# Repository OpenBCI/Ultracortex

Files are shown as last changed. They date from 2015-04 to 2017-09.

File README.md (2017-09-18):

# Ultracortex

Ultracortex Mark Numbers (aka versions)

* [Mark 1](https://github.com/OpenBCI/Ultracortex/tree/master/Mark_1) - designed, printed, assembled, & modeled (April 2015)
* [Mark 2](https://github.com/OpenBCI/Ultracortex/tree/master/Mark_2) - designed, printed, assembled, & tested (May-June 2015)
* [Mark 3](https://github.com/OpenBCI/Ultracortex/tree/master/Mark_3) - designed, printed, assembled, & tested (July-September 2015)
* [Mark III "Nova" & "Supernova"](https://github.com/OpenBCI/Ultracortex/tree/master/Mark_III_Nova) - designed, printed, assembled, & tested (April 2016)
* [Mark III "Nova" & "Supernova" (REVISED)](https://github.com/OpenBCI/Ultracortex/tree/master/Mark_III_Nova_REVISED) - designed, printed, assembled, & tested (June 2016)
* [**CURRENT**] [Mark IV](https://github.com/OpenBCI/Ultracortex/tree/master/Mark_IV) - designed, printed, assembled, & tested (January 2017)

The Ultracortex is an open-source, 3D-printable headset intended to work with the [OpenBCI system](http://openbci.com/). It is capable of recording research-grade brain activity (EEG), muscle activity (EMG), and heart activity (ECG). The Ultracortex is under constant iteration. If you print/assemble your own Ultracortex, we would love to hear your feedback. Send us an email at [contact@openbci.com](mailto:contact@openbci.com) or Tweet at us ([@Ultracortex](https://twitter.com/Ultracortex) & [@OpenBCI](https://twitter.com/OpenBCI))!

Designers & Engineers:

* [Aaron Trocola (aka Threeform)](http://threeformfashion.com/)
* [Conor Russomanno](https://twitter.com/russomanno15)
* [Joel Murphy (aka SafeForRobots)](https://twitter.com/safeforrobots)
* [Aaron Lehr](http://aaronlehr.com/portfolio/)

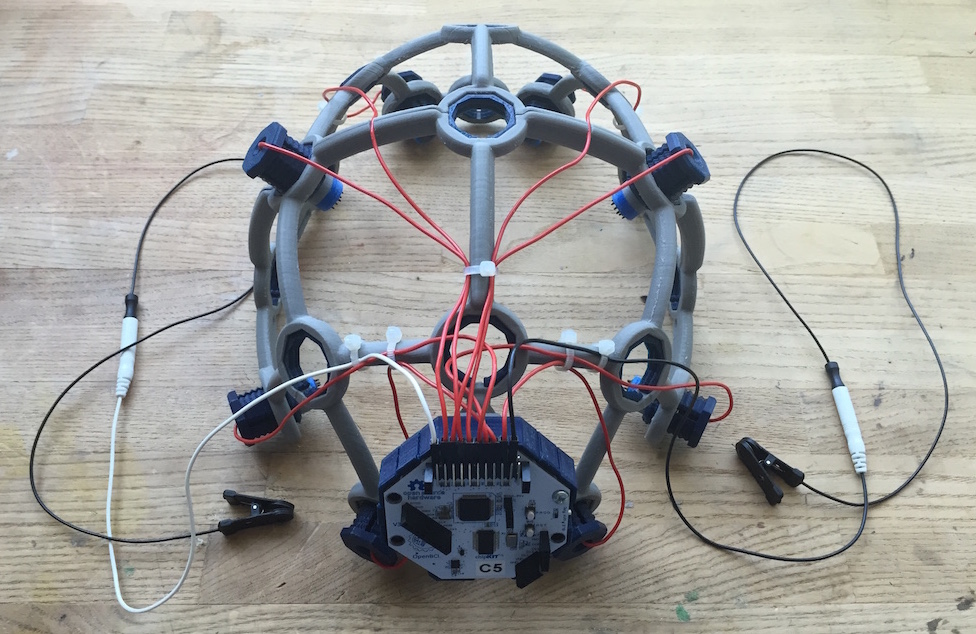
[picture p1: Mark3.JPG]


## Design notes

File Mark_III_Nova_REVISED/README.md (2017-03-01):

#Ultracortex Mark III "Nova" & "Supernova" (REVISED)

*Development Period: June 2016*

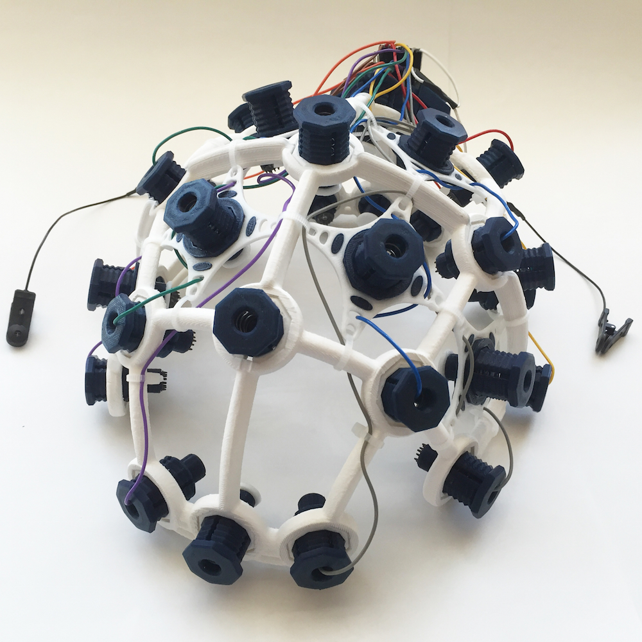
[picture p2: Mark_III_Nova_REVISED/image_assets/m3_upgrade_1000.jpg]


####Complete Ultracortex Mark 3 kits are [available for sale](http://openbci.myshopify.com/collections/frontpage/products/ultracortex-mark-3-eeg-headset-kit-assembly-required) in the OpenBCI Online Store!

The Ultracortex is an open-source, 3D-printable headset intended to work with the [OpenBCI system](http://openbci.com/). It is capable of recording research-grade brain activity (EEG), muscle activity (EMG), and heart activity (ECG). The Ultracortex is under constant iteration. If you print/assemble your own Ultracortex, we would love to hear your feedback. Send us an email at [contact@openbci.com](mailto:contact@openbci.com) or Tweet at us ([@Ultracortex](https://twitter.com/Ultracortex) & [@OpenBCI](https://twitter.com/OpenBCI))!

Designers & Engineers:

* [Aaron Trocola (aka Threeform)](http://threeformfashion.com/)
* [Conor Russomanno](https://twitter.com/russomanno15)
* [Joel Murphy (aka SafeForRobots)](https://twitter.com/safeforrobots)

## THE COMPLETE ULTRACORTEX

**Note:** the part quantities listed below assume you are making an electrode holder for all 21 nodes of the Ultracortex Mark 3. In reality, you will likely have only 8 or 16 electrodes, depending on whether you are working with the [OpenBCI 32bit Board](http://openbci.myshopify.com/collections/frontpage/products/openbci-32-bit-board-kit) (8 channels) or the [OpenBCI 16-channel R&D Kit](http://openbci.myshopify.com/collections/frontpage/products/openbci-16-channel-r-d-kit) (16 channels). You may only want to create as many electrode units as you have channels, and then add more as necessary. In general, more electrodes will distribute the downward scalp pressure, increasing comfort.

###3D-printed Parts:

* [FRAME](https://github.com/OpenBCI/Ultracortex/tree/master/Mark_III_Nova_REVISED/STLs/FRAME) (head circumference: small = 50-55cm, medium = 55-60cm, large = 60-65cm)
	* FRAME_FRONT (**x1**) — .STLs ([small](https://github.com/OpenBCI/Ultracortex/raw/master/Mark_III_Nova_REVISED/STLs/FRAME/small/SMALL_FRONT-M3_Nova_Revised.stl) / [medium](https://github.com/OpenBCI/Ultracortex/raw/master/Mark_III_Nova_REVISED/STLs/FRAME/medium/MEDIUM_FRONT-M3_Nova_Revised.stl) / [large](https://github.com/OpenBCI/Ultracortex/raw/master/Mark_III_Nova_REVISED/STLs/FRAME/large/LARGE_FRONT-M3_Nova_Revised.stl))
	* FRAME_BACK (**x1**) — .STLs ([small](https://github.com/OpenBCI/Ultracortex/raw/master/Mark_III_Nova_REVISED/STLs/FRAME/small/SMALL_BACK-M3_Nova_Revised.stl) / [medium](https://github.com/OpenBCI/Ultracortex/raw/master/Mark_III_Nova_REVISED/STLs/FRAME/medium/MEDIUM_BACK-M3_Nova_Revised.stl) / [large](https://github.com/OpenBCI/Ultracortex/raw/master/Mark_III_Nova_REVISED/STLs/FRAME/large/LARGE_BACK-M3_Nova_Revised.stl))
* [MECH_PARTS](https://github.com/OpenBCI/Ultracortex/tree/master/Mark_III_Nova_REVISED/STLs/MECH_PARTS)
	* [OCTANUT](https://github.com/OpenBCI/Ultracortex/tree/master/Mark_III_Nova_REVISED/STLs/MECH_PARTS/OCTANUT) (**x21**) — .STLs ([tight](https://github.com/OpenBCI/Ultracortex/raw/master/Mark_III_Nova_REVISED/STLs/MECH_PARTS/OCTANUT/OCTANUT-TIGHT.stl) / [normal](https://github.com/OpenBCI/Ultracortex/raw/master/Mark_III_Nova_REVISED/STLs/MECH_PARTS/OCTANUT/OCTANUT-NORMAL.stl) / [loose](https://github.com/OpenBCI/Ultracortex/raw/master/Mark_III_Nova_REVISED/STLs/MECH_PARTS/OCTANUT/OCTANUT-LOOSE.stl)) (Choose normal first / if it is too tight for the OCTABOLT, choose loose / if it is too loose for the OCTABOLT, choose tight)
	* [OCTABOLT](https://github.com/OpenBCI/Ultracortex/blob/master/Mark_III_Nova_REVISED/STLs/MECH_PARTS/OCTABOLT_20.stl) (**x21**) — [.STL download link](https://github.com/OpenBCI/Ultracortex/raw/master/Mark_III_Nova_REVISED/STLs/MECH_PARTS/OCTABOLT_20.stl)
	* [OCTARING](https://github.com/OpenBCI/Ultracortex/blob/master/Mark_III_Nova_REVISED/STLs/MECH_PARTS/OCTARING.stl) (**x21**) — [.STL download link](https://github.com/OpenBCI/Ultracortex/raw/master/Mark_III_Nova_REVISED/STLs/MECH_PARTS/OCTARING.stl)
	* [ELECTRODE_HOLDER](https://github.com/OpenBCI/Ultracortex/blob/master/Mark_III_Nova_REVISED/STLs/MECH_PARTS/E_HOLDER.stl) (**x21**) — [.STL download link](https://github.com/OpenBCI/Ultracortex/raw/master/Mark_III_Nova/STLs/MECH_PARTS/E_HOLDER.stl)
	* [QUADSTAR](https://github.com/OpenBCI/Ultracortex/blob/master/Mark_III_Nova_REVISED/STLs/MECH_PARTS/QUADSTAR.stl) (**x21**) — [.STL download link](https://github.com/OpenBCI/Ultracortex/raw/master/Mark_III_Nova/STLs/MECH_PARTS/QUADSTAR.stl)
	* [Comfy Insert](https://github.com/OpenBCI/Ultracortex/blob/master/Mark_III_Nova_REVISED/STLs/MECH_PARTS/Comfy_Insert.stl) (**x21**) — [.STL download link](https://github.com/OpenBCI/Ultracortex/raw/master/Mark_III_Nova/STLs/MECH_PARTS/Comfy_Insert.stl)	
* [BOARD_HOLDER](https://github.com/OpenBCI/Ultracortex/blob/master/Mark_III_Nova_REVISED/STLs/HOLDER_AND_COVER/BOARD_HOLDER.stl) (**x1**) — [.STL download link](https://github.com/OpenBCI/Ultracortex/raw/master/Mark_III_Nova/STLs/HOLDER_AND_COVER/BOARD_HOLDER.stl)
* BOARD_COVER (**x1**) — choose STANDARD or ADVANCED
	* [STANDARD](https://github.com/OpenBCI/Ultracortex/blob/master/Mark_III_Nova_REVISED/STLs/HOLDER_AND_COVER/BOARD_COVER_STANDARD.stl) — [.STL download link](https://github.com/OpenBCI/Ultracortex/raw/master/Mark_III_Nova/STLs/HOLDER_AND_COVER/BOARD_COVER_STANDARD.stl)
	* [ADVANCED](https://github.com/OpenBCI/Ultracortex/blob/master/Mark_III_Nova_REVISED/STLs/HOLDER_AND_COVER/BOARD_COVER_ADVANCED.stl) (for extra hardware accessibility / if you've soldered on your header rows) — [.STL download link](https://github.com/OpenBCI/Ultracortex/raw/master/Mark_III_Nova/STLs/HOLDER_AND_COVER/BOARD_COVER_ADVANCED.stl)

###Non-printed Parts:
 	
* Additional Hardware:
	* **Suggested Spring 1** listed below (**x21**)
	* **Suggested Spring 2** listed below (**x5**)
	* **Suggested Nuts** listed below (**x42**)
	* **Suggested Bolts** listed below (**x21**)
	* 1/4" #4 Drive Screw listed below (**x8**) for mounting the BOARD_HOLDER and OpenBCI Board
* Wiring (**x21**)
	* We strip apart the [Gold Cup Electrodes](http://openbci.myshopify.com/collections/frontpage/products/openbci-gold-cup-electrodes) or from the Touch-Proof Connector cable that comes with an [OpenBCI 32bit Board Kit](http://openbci.myshopify.com/collections/frontpage/products/openbci-32-bit-board-kit).
* Dry electrodes by Florida Research Instruments
	* (**18x**) Dry (spikey) electrodes to be installed in Ultracortex nodes with hair: [Disposable / Reusable Dry EEG Electrode ($0.60 each at 50+ quantity purchase) ](http://fri-fl-shop.com/product/tde-200/)
	* (**3x**) Dry (non-spikey) electrodes to be installed in Ultracortex nodes without hair (forehead, for instance): [Disposable / Reusable Cup Wet/Dry EEG Electrode ($10.00 for 15) ](http://fri-fl-shop.com/product/disposable-reusable-dry-eeg-electrode-quantity-of-15-tde-200a1/)
	* (**2x**) Ear Clip electrode (for reference): [TDI-430 Silver-Silver Chloride Ear Clip Electrode ($19.95 each)](http://fri-fl-shop.com/product/td-430-silver-disc-electrode-ear-clip/)
* (**1x**) An [OpenBCI 32bit Board](http://openbci.myshopify.com/collections/frontpage/products/openbci-32-bit-board-kit) or an [OpenBCI 16-channel R&D Kit](http://openbci.myshopify.com/collections/frontpage/products/openbci-16-channel-r-d-kit)
* (**1x**) Lithium Ion Rechargeable Battery Pack (~500mAh) — [Sparkfun](https://www.sparkfun.com/products/10718) or [Adafruit](http://www.adafruit.com/products/1578)
* (**1x**) [A charger for your battery pack](https://www.adafruit.com/products/1304)
* (**~10x**) [Zip tie](http://www.amazon.com/Black-Zip-Tie-100-Bag/dp/B0001IMMJI)

## THE COMPLETE ULTRACORTEX (w/ PICTURES)

###3D-printed Parts:

####(1x) FRAME

* [FRAME](https://github.com/OpenBCI/Ultracortex/tree/master/Mark_III_Nova_REVISED/STLs/FRAME) (head circumference: small = 50-55cm, medium = 55-60cm, large = 60-65cm)
	* FRAME_FRONT (**x1**) — .STLs ([small](https://github.com/OpenBCI/Ultracortex/raw/master/Mark_III_Nova_REVISED/STLs/FRAME/small/SMALL_FRONT-M3_Nova_Revised.stl) / [medium](https://github.com/OpenBCI/Ultracortex/raw/master/Mark_III_Nova_REVISED/STLs/FRAME/medium/MEDIUM_FRONT-M3_Nova_Revised.stl) / [large](https://github.com/OpenBCI/Ultracortex/raw/master/Mark_III_Nova_REVISED/STLs/FRAME/large/LARGE_FRONT-M3_Nova_Revised.stl))
	* FRAME_BACK (**x1**) — .STLs ([small](https://github.com/OpenBCI/Ultracortex/raw/master/Mark_III_Nova_REVISED/STLs/FRAME/small/SMALL_FRONT-M3_Nova_Revised.stl) / [medium](https://github.com/OpenBCI/Ultracortex/raw/master/Mark_III_Nova_REVISED/STLs/FRAME/medium/MEDIUM_BACK-M3_Nova_Revised.stl) / [large](https://github.com/OpenBCI/Ultracortex/raw/master/Mark_III_Nova_REVISED/STLs/FRAME/large/LARGE_BACK-M3_Nova_Revised.stl))

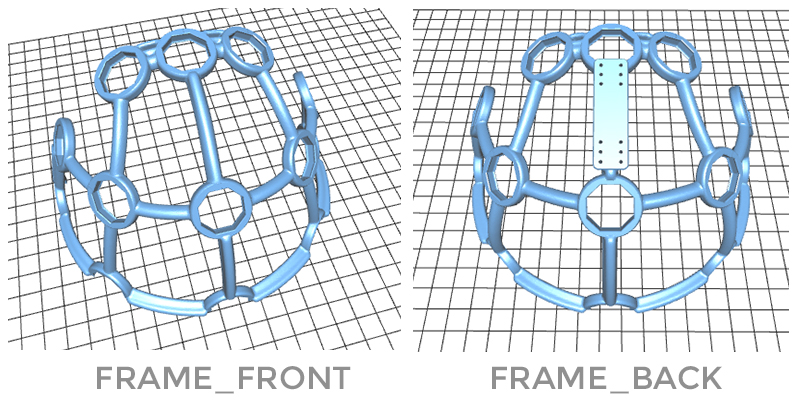
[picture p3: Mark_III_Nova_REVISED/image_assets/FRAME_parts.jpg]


####(21x) MECH_PARTS

* [MECH_PARTS](https://github.com/OpenBCI/Ultracortex/tree/master/Mark_III_Nova_REVISED/STLs/MECH_PARTS)
	* [OCTANUT](https://github.com/OpenBCI/Ultracortex/tree/master/Mark_III_Nova_REVISED/STLs/MECH_PARTS/OCTANUT) (**x21**) — .STLs ([tight](https://github.com/OpenBCI/Ultracortex/raw/master/Mark_III_Nova_REVISED/STLs/MECH_PARTS/OCTANUT/OCTANUT-TIGHT.stl) / [normal](https://github.com/OpenBCI/Ultracortex/raw/master/Mark_III_Nova_REVISED/STLs/MECH_PARTS/OCTANUT/OCTANUT-NORMAL.stl) / [loose](https://github.com/OpenBCI/Ultracortex/raw/master/Mark_III_Nova_REVISED/STLs/MECH_PARTS/OCTANUT/OCTANUT-LOOSE.stl)) (Choose normal first / if it is too tight for the OCTABOLT, choose loose / if it is too loose for the OCTABOLT, choose tight)
	* [OCTABOLT](https://github.com/OpenBCI/Ultracortex/blob/master/Mark_III_Nova_REVISED/STLs/MECH_PARTS/OCTABOLT_20.stl) (**x21**) — [.STL download link](https://github.com/OpenBCI/Ultracortex/raw/master/Mark_III_Nova_REVISED/STLs/MECH_PARTS/OCTABOLT_20.stl)
	* [OCTARING](https://github.com/OpenBCI/Ultracortex/blob/master/Mark_III_Nova_REVISED/STLs/MECH_PARTS/OCTARING.stl) (**x21**) — [.STL download link](https://github.com/OpenBCI/Ultracortex/raw/master/Mark_III_Nova_REVISED/STLs/MECH_PARTS/OCTARING.stl)
	* [ELECTRODE_HOLDER](https://github.com/OpenBCI/Ultracortex/blob/master/Mark_III_Nova_REVISED/STLs/MECH_PARTS/E_HOLDER.stl) (**x21**) — [.STL download link](https://github.com/OpenBCI/Ultracortex/raw/master/Mark_III_Nova/STLs/MECH_PARTS/E_HOLDER.stl)
	* [QUADSTAR](https://github.com/OpenBCI/Ultracortex/blob/master/Mark_III_Nova_REVISED/STLs/MECH_PARTS/QUADSTAR.stl) (**x21**) — [.STL download link](https://github.com/OpenBCI/Ultracortex/raw/master/Mark_III_Nova/STLs/MECH_PARTS/QUADSTAR.stl)
	* [Comfy Insert](https://github.com/OpenBCI/Ultracortex/blob/master/Mark_III_Nova_REVISED/STLs/MECH_PARTS/Comfy_Insert.stl) (**x21**) — [.STL download link](https://github.com/OpenBCI/Ultracortex/raw/master/Mark_III_Nova/STLs/MECH_PARTS/Comfy_Insert.stl)	

####(1x) BOARD_HOLDER

* [BOARD_HOLDER](https://github.com/OpenBCI/Ultracortex/blob/master/Mark_III_Nova_REVISED/STLs/HOLDER_AND_COVER/BOARD_HOLDER.stl) — [.STL download link](https://github.com/OpenBCI/Ultracortex/raw/master/Mark_III_Nova/STLs/HOLDER_AND_COVER/BOARD_COVER_STANDARD.stl)	
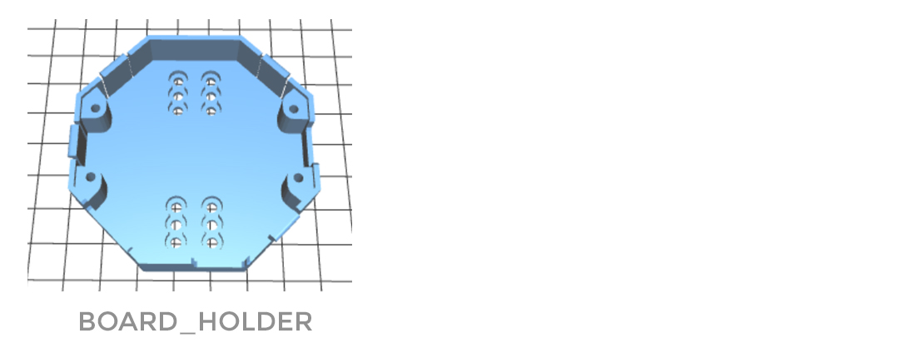
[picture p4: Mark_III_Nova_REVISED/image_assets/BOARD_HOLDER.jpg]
 

####(1x) BOARD_COVER

* BOARD_COVER (**x1**) — choose STANDARD or ADVANCED
	* [STANDARD](https://github.com/OpenBCI/Ultracortex/blob/master/Mark_III_Nova_REVISED/STLs/HOLDER_AND_COVER/BOARD_COVER_STANDARD.stl) — [.STL download link](https://github.com/OpenBCI/Ultracortex/raw/master/Mark_III_Nova/STLs/HOLDER_AND_COVER/BOARD_COVER_STANDARD.stl)
	* [ADVANCED](https://github.com/OpenBCI/Ultracortex/blob/master/Mark_III_Nova_REVISED/STLs/HOLDER_AND_COVER/BOARD_COVER_ADVANCED.stl) (for extra hardware accessibility / if you've soldered on your header rows) — [.STL download link](https://github.com/OpenBCI/Ultracortex/raw/master/Mark_III_Nova/STLs/HOLDER_AND_COVER/BOARD_COVER_ADVANCED.stl)

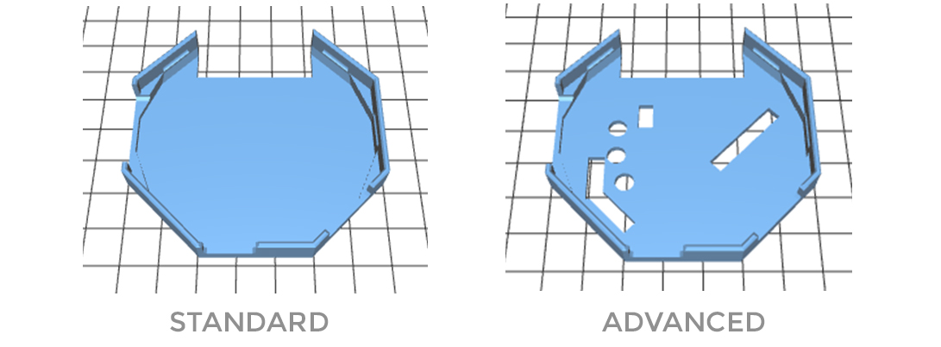
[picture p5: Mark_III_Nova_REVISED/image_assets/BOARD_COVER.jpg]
 

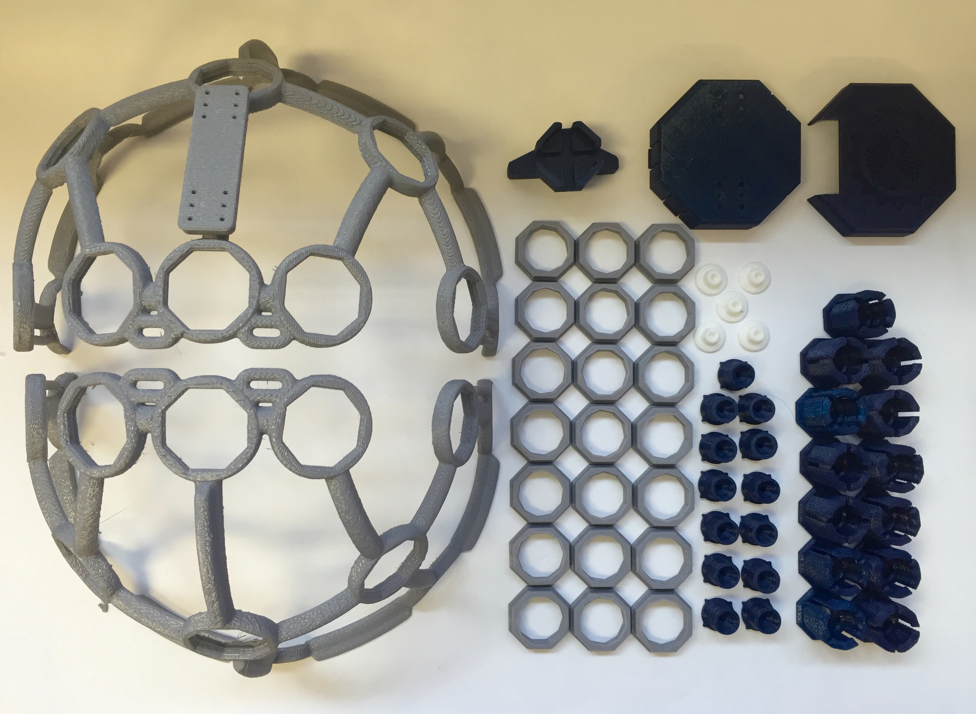
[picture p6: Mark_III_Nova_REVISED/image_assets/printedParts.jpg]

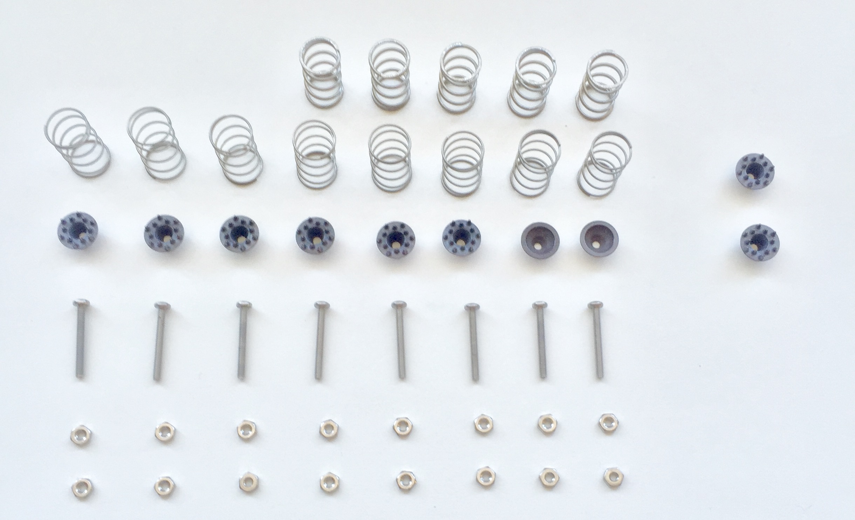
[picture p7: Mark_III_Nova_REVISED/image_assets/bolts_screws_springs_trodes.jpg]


###Non-printed Parts:

####Suggested springs: 

* Suggested Spring 1 (**x21**) — aka "Weak Spring" — [Century Spring Corp. Stock #: U-4](http://cad.centuryspring.com/db/service?domain=century&command=showProduct&category=compression&product=U-4) — this spring is not as strong as spring 2. We use it to mount the electrodes. The low "Rate" (1.3 lbs/in) makes it more forgiving and comfortable when holding the spikey electrode against your head. This process is described in more detail below (in the "Assembly Instructions" section).

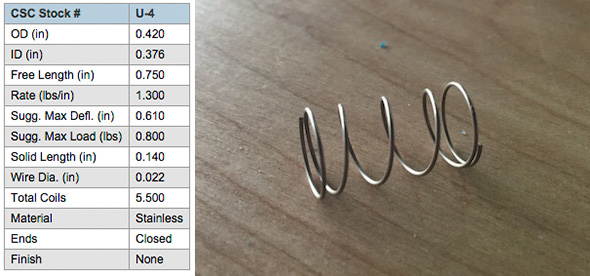
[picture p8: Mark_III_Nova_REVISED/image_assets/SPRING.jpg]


* Suggested Spring 2 (**x5**) — aka "Strong Spring" — [Century Spring Corp. Stock #: S-845](http://cad.centuryspring.com/db/service?domain=century&command=showProduct&category=compression&product=S-845) — this spring has a much stronger "Rate" (14 lb/in). This makes is ideal to act as a standoff at locations where you do not have a spikey electrode. This process is described in more detail below (in the "Assembly Instructions" section).

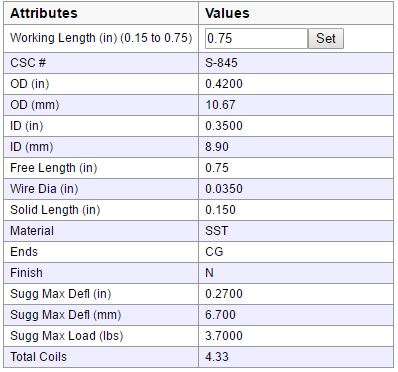
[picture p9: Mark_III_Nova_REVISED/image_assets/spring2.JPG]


####Suggested nuts/bolts:

We use small stainless steel screws and hex nuts to fasten the FRI electrodes (listed above) to the 3D-printed electrode mount components &  wiring that connects the electrodes back to the OpenBCI board. We used stripped [Gold Cup Electrodes](http://openbci.myshopify.com/collections/frontpage/products/openbci-gold-cup-electrodes) as the cabling, by removing the gold cup with a wire cutter and looping the exposed wire around the screw between the two tightened hex nuts (as seen in the picture below).

* (**21x**) [Stainless Steel Pan Head Phillips Machine Screw, 2-56 Thread, 3/4" Length ($5.70 per pack of 50)](http://www.mcmaster.com/#91772a084/=11zdicn)
* (**42x**) [Stainless Steel Hex Nut, 2-56 Thread Size, 3/16" Wide, 1/16" High](http://www.mcmaster.com/#91841a003/=xzahv0)



####Suggested screws for fastening BOARD_MOUNT & OpenBCI Board

* (**8x**) [#4 Drive Screw](http://www.mcmaster.com/#90077a106/=yysd5f)



####Wiring

* (**21x**) We strip apart the [Gold Cup Electrodes](http://openbci.myshopify.com/collections/frontpage/products/openbci-gold-cup-electrodes)) or the Touch-Proof Connector cable that comes with an [OpenBCI 32bit Board Kit](http://openbci.myshopify.com/collections/frontpage/products/openbci-32-bit-board-kit).

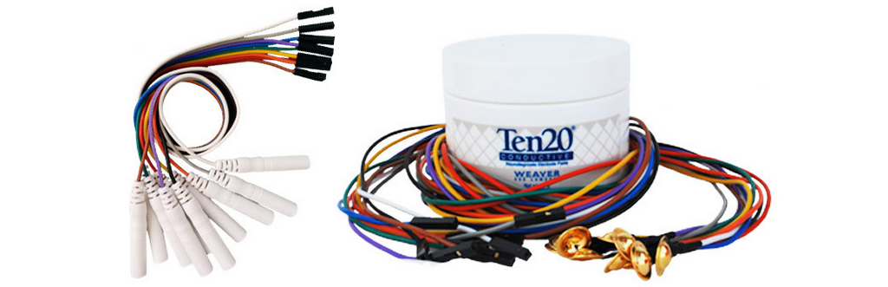
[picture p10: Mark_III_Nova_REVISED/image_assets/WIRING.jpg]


####Dry electrodes by Florida Research Instruments

* (**18x**) Dry (spikey) electrodes to be installed in Ultracortex nodes with hair: [Disposable / Reusable Dry EEG Electrode ($0.60 each at 50+ quantity purchase) ](http://fri-fl-shop.com/product/tde-200/)
* (**3x**) Dry (non-spikey) electrodes to be installed in Ultracortex nodes without hair (forehead, for instance): [Disposable / Reusable Cup Wet/Dry EEG Electrode ($10.00 for 15) ](http://fri-fl-shop.com/product/disposable-reusable-dry-eeg-electrode-quantity-of-15-tde-200a1/)
* (**2x**) Ear Clip electrode (for reference): [TDI-430 Silver-Silver Chloride Ear Clip Electrode ($19.95 each)](http://fri-fl-shop.com/product/td-430-silver-disc-electrode-ear-clip/)

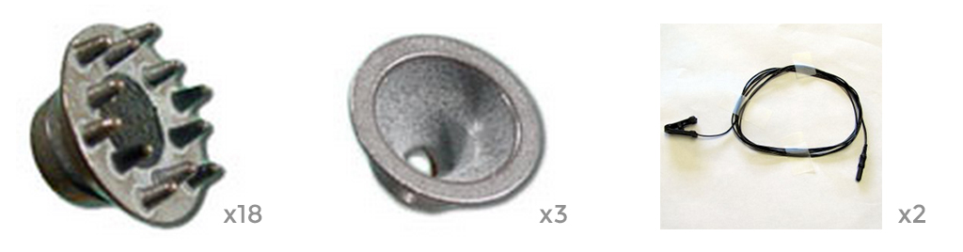
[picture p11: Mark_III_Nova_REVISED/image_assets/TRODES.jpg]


####(1x) An [OpenBCI 32bit Board](http://openbci.myshopify.com/collections/frontpage/products/openbci-32-bit-board-kit) (8 electrode channels) or an [OpenBCI 16-channel R&D Kit](http://openbci.myshopify.com/collections/frontpage/products/openbci-16-channel-r-d-kit) (16 electrode channels)

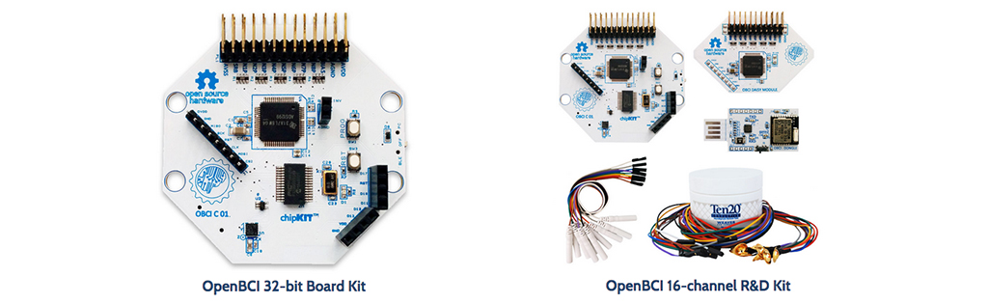
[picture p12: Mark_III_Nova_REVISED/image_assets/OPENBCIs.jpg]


####(**1x**) ~500mAh lithium ion rechargeable battery pack ([Sparkfun](https://www.sparkfun.com/products/10718) or [Adafruit](http://www.adafruit.com/products/1578)) & (**1x**) [A charger for your battery pack](https://www.adafruit.com/products/1304)

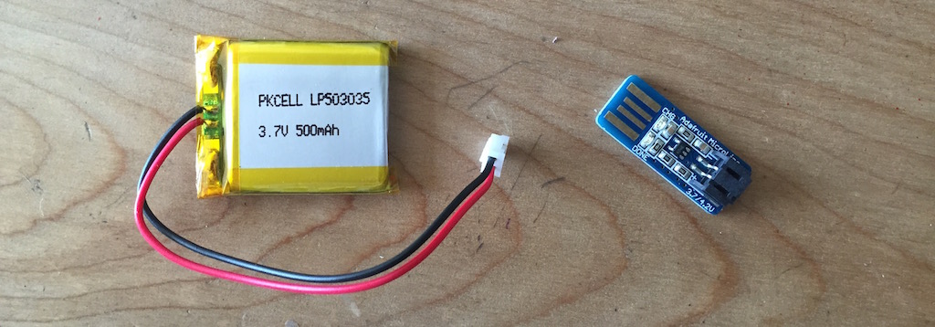
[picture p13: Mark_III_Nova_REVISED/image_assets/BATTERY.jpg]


#### (**~10x**) [Zip tie](http://www.amazon.com/Black-Zip-Tie-100-Bag/dp/B0001IMMJI)

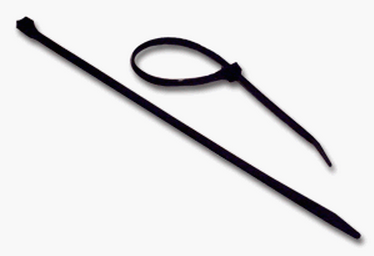
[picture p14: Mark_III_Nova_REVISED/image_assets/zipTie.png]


## SUGGESTED PRINT SETTINGS

* FRAME_FRONT & FRAME_BACK
	* Material: PLA
	* Supports: YES
	* Raft: hopefully NO (but if supports aren't sticking, try the raft)
	* Infill: 20%
	* Layer Height: 0.2mm
	* Number of Shells: 3
	* Speed while extruding: 50-70% (slow it down if possible; these parts are detailed)
* MECH_PARTS (OCTANUT / BOLT / SPRING_CASING / ELECTRODE_HOLDER)
	* Material: PLA
	* Supports: NO
	* Raft: NO
	* Infill: 20%
	* Layer Height: 0.2mm
	* Number of Shells: 3
	* Speed while extruding: 50-70% (slow it down if possible; these parts are detailed)
* BOARD_MOUNT, BOARD_COVER_STANDARD, & BOARD_COVER_ADVANCED
	* Material: PLA
	* Supports: NO
	* Raft: NO
	* Infill: 20%
	* Layer Height: 0.2mm
	* Number of Shells: 3
	* Speed while extruding: 50-70% (slow it down if possible; these parts are detailed)
* QUAD_STAR
 	* Material: [NinjaFlex](https://ninjatek.com/products/filaments/ninjaflex/) or [SemiFlex](https://ninjatek.com/products/filaments/semiflex/)
	* Supports: NO
	* Raft: NO
	* Infill: 10%
	* Layer Height: 0.27mm (or 0.3mm)
	* Number of Shells: 2
	* Speed while extruding: 30-50% (slow it down if possible; these parts are detailed)
	* Print Temperature: 230-250C (we get more consistant prints when printing at higher temperatures, but it gets stringy)

## RECOMMENDED ASSEMBLY TOOLS

1. [Loctite Super Glue w/ Cyanoacrylate](http://www.amazon.com/Loctite-1365882-20-Gram-Bottle-Professional/dp/B004Y960MU/ref=sr_1_1?s=automotive&ie=UTF8&qid=1440204266&sr=1-1&keywords=loctite+cyanoacrylate&pebp=1440204267936&perid=0HJQ0FB9G4J9SEBQBVGA)
2. coarse flat & circular files (for removing support artifacts)
3. medium sand paper
4. exacto blade
5. philips head screw driver
6. wire cutters
7. needle-nose pliers
8. snippers

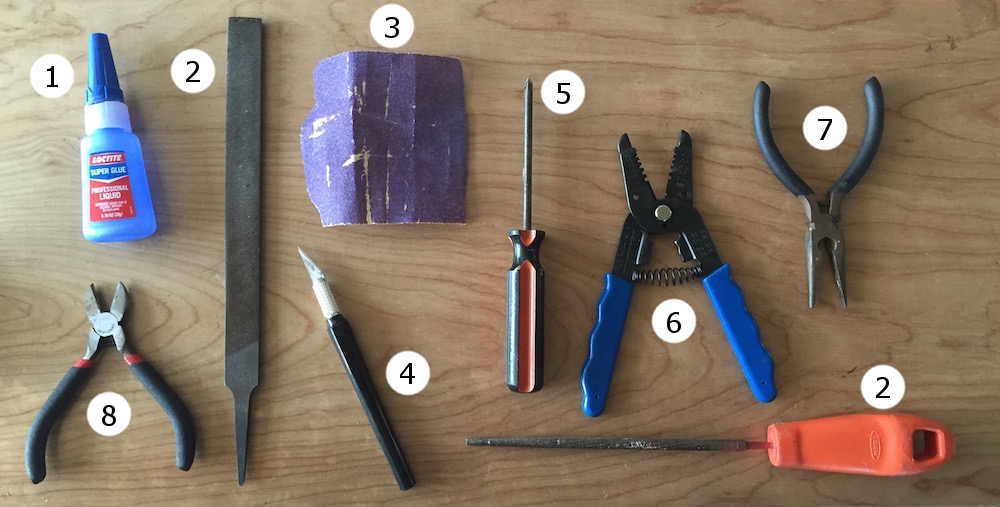
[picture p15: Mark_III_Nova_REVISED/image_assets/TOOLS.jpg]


## ASSEMBLY INSTRUCTIONS

### Remove residual support material & print flaws

Use sand paper, a file, and snippers to clean your FRAME and other 3D-printed parts. The most important part of this process is that you thoroughly clean out the frames nodes where you will place your OCTANUT pieces.

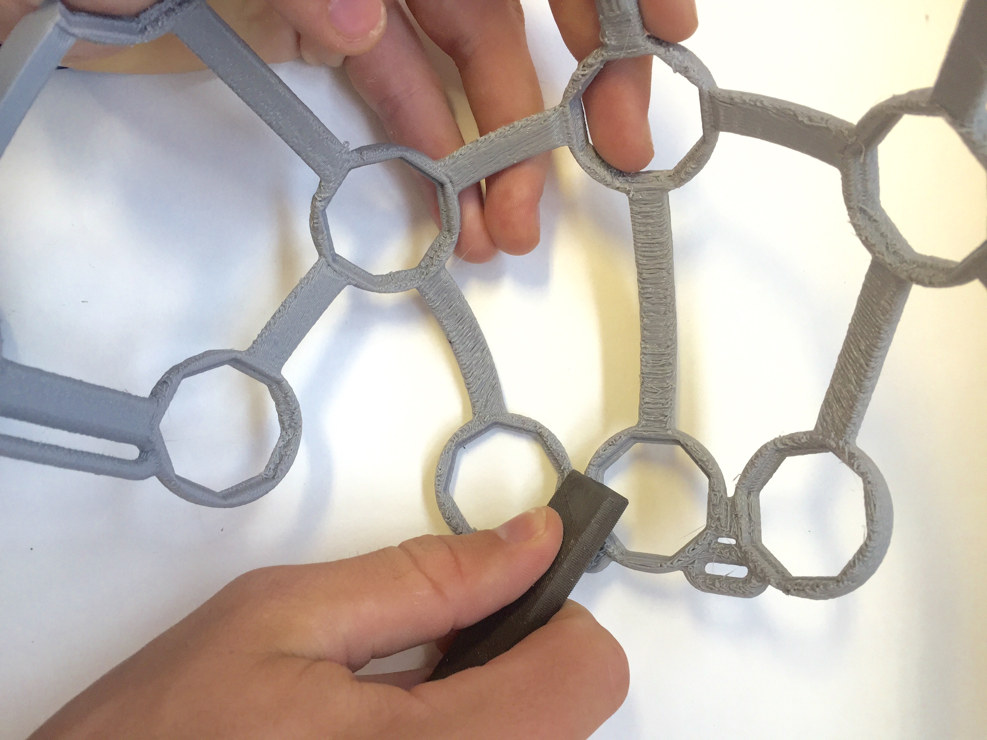
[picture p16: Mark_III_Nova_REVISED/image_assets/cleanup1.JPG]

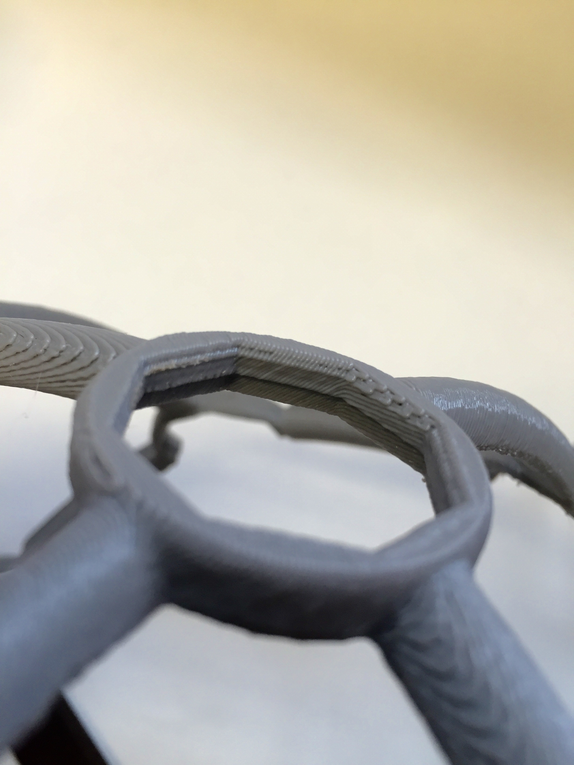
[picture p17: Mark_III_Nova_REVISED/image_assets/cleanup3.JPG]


### Glue the FRAME together

Carefully, glue the FRAME_FRONT and FRAME_BACK together with your Cyanoacrylate super glue. The best way to do this is to place both halves of the frame on a level surface and carefully bring them together. Be sure to be precise; it's VERY difficult to pull the pieces apart once you've put them together.

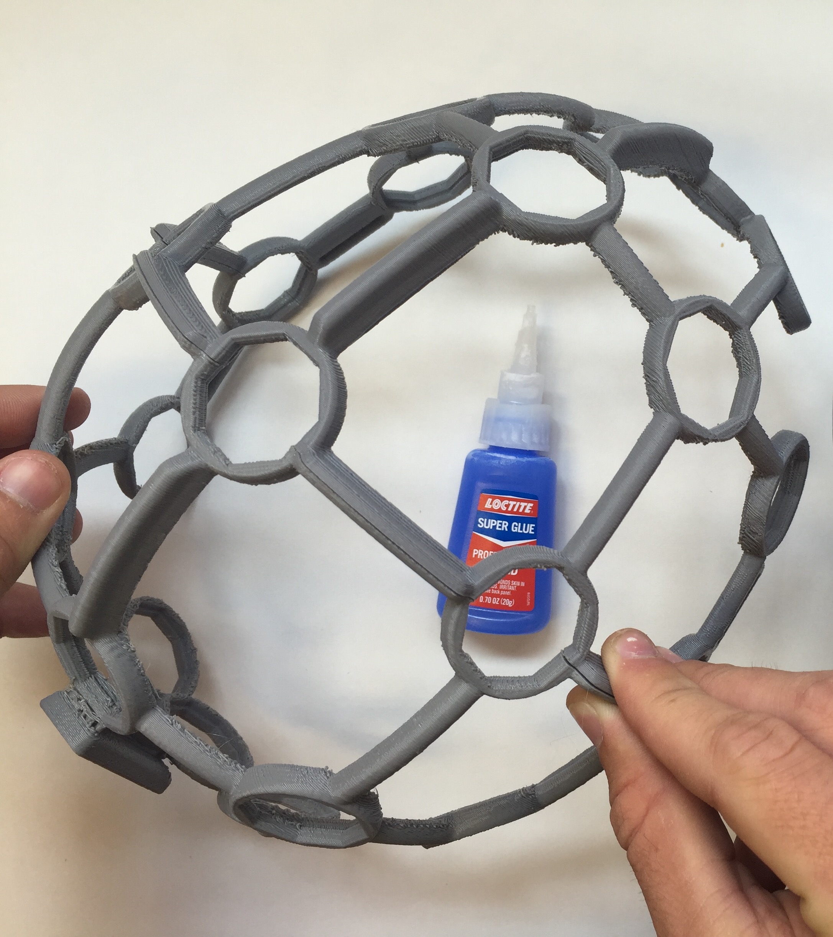
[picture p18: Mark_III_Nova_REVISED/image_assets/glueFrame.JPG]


### Mount the OpenBCI BOARD_HOLDER

First, use a 1/16" drillbit to expand the holes on the Ultracortex frame. This will make it easier to screw the BOARD_HOLDER on the frame.

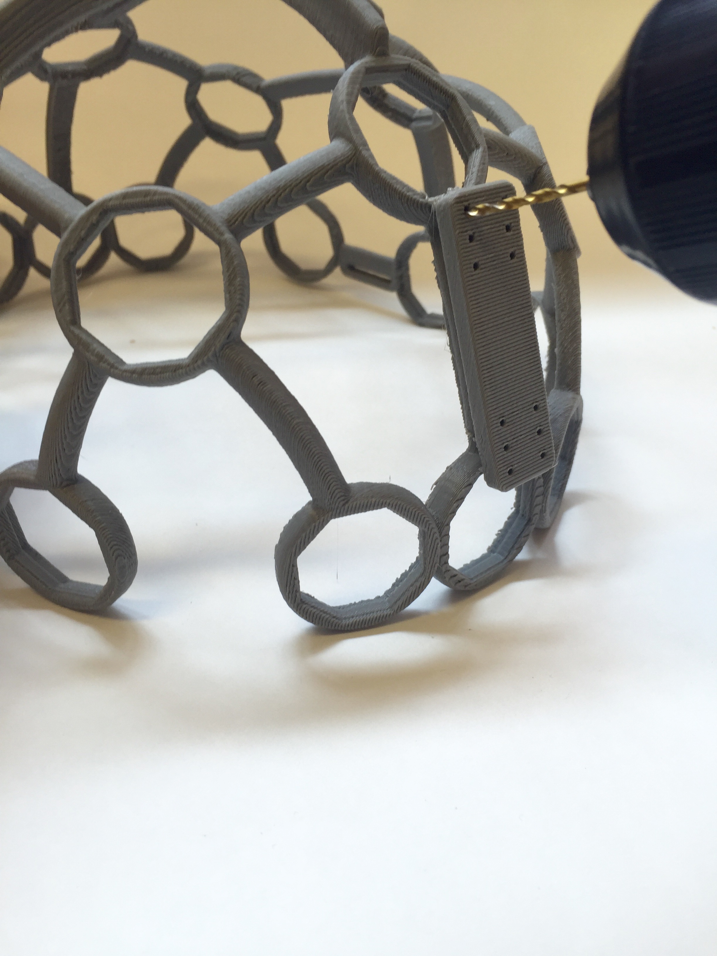
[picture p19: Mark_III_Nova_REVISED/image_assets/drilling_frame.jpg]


Use four #4 Drive Screws to mount the BOARD_HOLDER to the FRAME. Make sure that the orientation of the BOARD_HOLDER matches that of the pictures below:

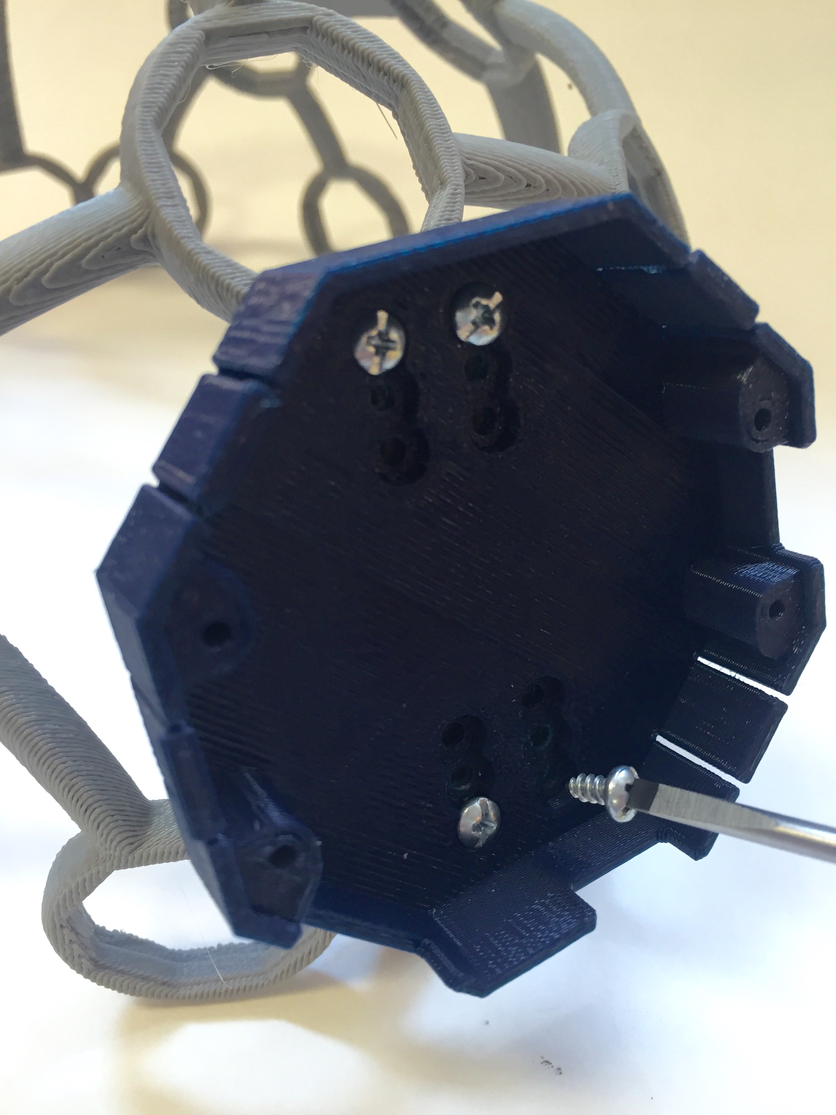
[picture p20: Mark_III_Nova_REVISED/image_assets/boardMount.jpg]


### Assemble the Comfort Nodes

In order to fit the OCTANUT pieces into the frame, you will need the Comfort Nodes in order to securely glue the OCTANUTs in place. 

You will need the following pieces:

-OCTABOLT

-Strong Spring

-ELECTRODE_HOLDER

-Comfort insert

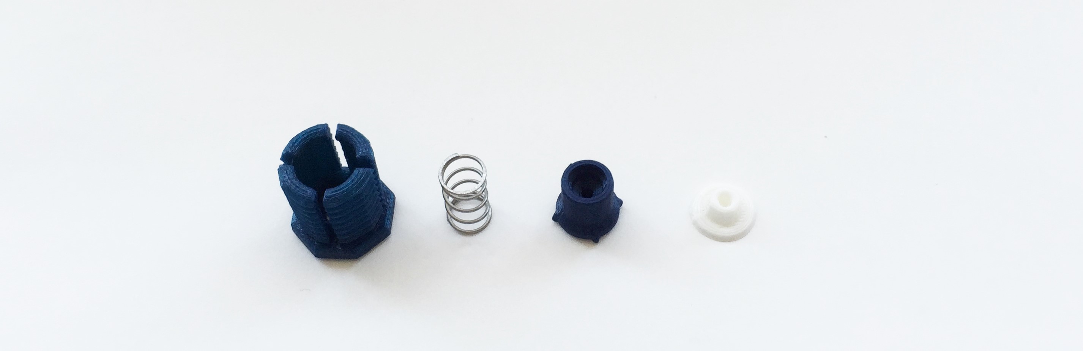
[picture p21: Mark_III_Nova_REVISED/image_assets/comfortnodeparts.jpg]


First, put the comfort insert into front of the ELECTRODE_HOLDER.
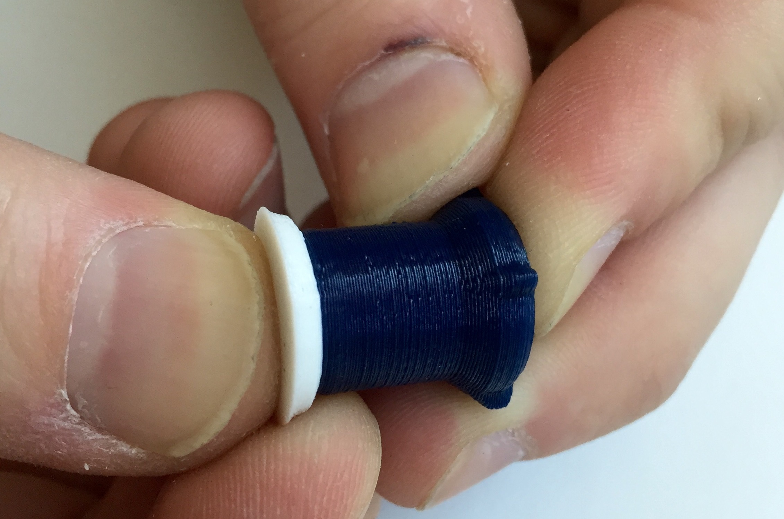
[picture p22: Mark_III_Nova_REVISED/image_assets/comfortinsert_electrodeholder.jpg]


Next, insert the spring into the back of the ELECTRODE_HOLDER.
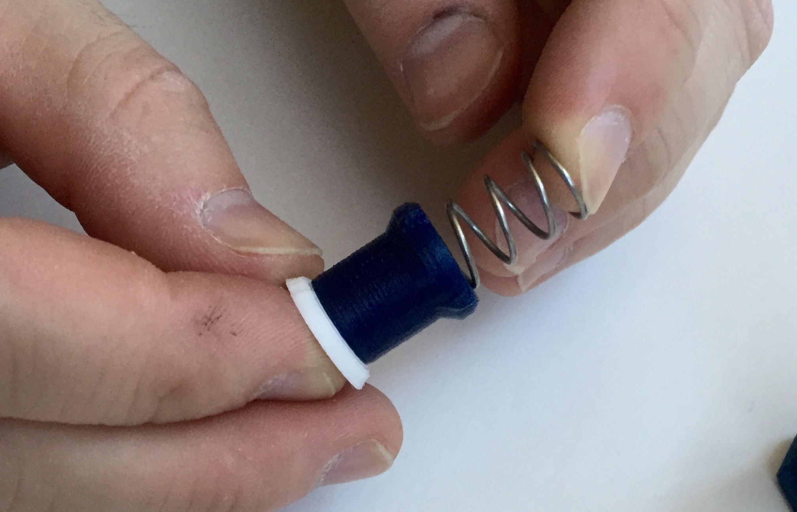
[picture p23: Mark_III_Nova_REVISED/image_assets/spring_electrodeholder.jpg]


Then, slide the OCTABOLT over the top:
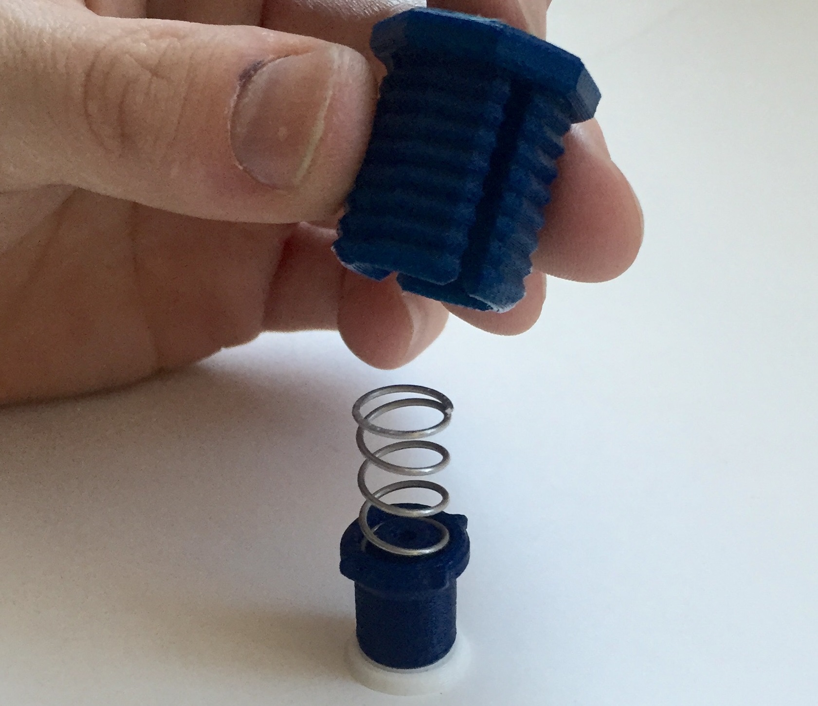
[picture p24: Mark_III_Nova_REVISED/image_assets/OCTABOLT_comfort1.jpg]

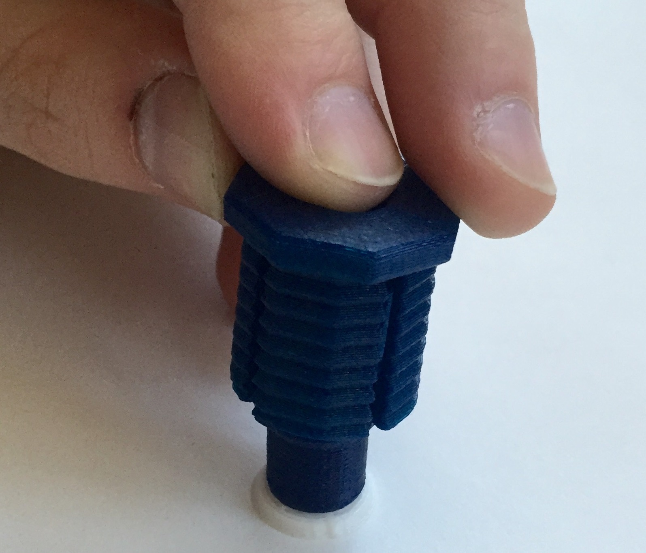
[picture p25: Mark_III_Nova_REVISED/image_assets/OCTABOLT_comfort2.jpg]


### Insert OCTANUT pieces (x21) into frame

**Note:** Before glueing the OCTANUT into the frame ensure, that it fits properly into the frame without glue.



For each OCTANUT, line the inner rim of frame with glue. Then insert the OCTANUT so that it is flush with the frame.



Your Ultracortex should now look like this:



### Embed OpenBCI into the Ultracortex

Connect your ~500 mAh lithium ion rechargeable batter to the back of your 32bit OpenBCI Board. Then fold the battery and its wires neatly behind the board before inserting the board into the BOARD_MOUNT. You can then use one of your #4 Drive Screws to secure the OpenBCI Board to the BOARD_MOUNT. Typically you don't need to use any #4 Drive Screws because the BOARD_COVER locks the OpenBCI Board in place, but in this case it's a good idea because you'll want to see where you're connecting your wires.





### Identify electrode locations

Before creating your electrode mounts, it's a good idea to think about where you may want to place the electrodes on the Ultracortex FRAME. The placement of the electrode may affect how long you make the wire between the electrode and where the OpenBCI is mounted, at the back of the frame.

The Ultracortex node locations are based on the [10-20 system](https://goo.gl/gSwYw), which is the internationally accepted standard for electrode placement in the context of EEG.

The images below indicates the default 10-20 electrode locations that the OpenBCI Graphical User Interface expects. This application is great for viewing/recording your EEG and can be found in our [OpenBCI_Processing](http://) repo. The blue nodes indicate the 8 default 10-20 locations (channels 1-8) of the 32bit Board. The red nodes indicate the default 10-20 locations of channels 9-16 when using the OpenBCI 16-channel R&D Kit. 

For the remainder of this tutorial, the blue nodes on the 10-20 system diagram (channels 1-8 of the OpenBCI default settings) will be used. The channel to 10-20 system correlations are as follows:

* Channel 1(N1P) - Fp1
* Channel 2(N2P) - Fp2
* Channel 3(N3P) - C3
* Channel 4(N4P) - C4
* Channel 5(N5P) - P7
* Channel 6(N6P) - P8
* Channel 7(N7P) - O1
* Channel 8(N8P) - O2



### Connect wiring to OpenBCI

Before shortening any of your wires, connect the female header of each wire to the N pin of channels 1-8, as indicated in the image to the lower right. The N pins are the ones closer to the OpenBCI Board. By default, the OpenBCI Board references these 8 pins with the SRB 2 pin (the bottom SRB pin).



### Measure, cut, and strip wires

For each wire, measure the distance between where it is connected to the OpenBCI Board and the node that it will terminate at on the Ultracortex frame. Give yourself 2-3 inches of slack (extra length), because you're going to strip the end of the wire, and you may want the extra slack to zip-tie/tape the wiring to the frame later on.

As mentioned above, if you're using the default OpenBCI electrode configuration, cut the wires so that they terminate at the following nodes:

* Channel 1(N1P) - Fp1
* Channel 2(N2P) - Fp2
* Channel 3(N3P) - C3
* Channel 4(N4P) - C4
* Channel 5(N5P) - P7
* Channel 6(N6P) - P8
* Channel 7(N7P) - O1
* Channel 8(N8P) - O2

After you're done measuring, cutting, and stripping your wires, disconnect them from the OpenBCI board. You will need the female header free so you can guide the springs and OCTANUT pieces into place in the following step. But remember which wire goes where!









### Assemble electrode mounts (x8 or x16)
**Note:** repeat the following steps as many times as necessary, depending upon your OpenBCI setup. In general, using more electrodes will distribute the downward scalp pressure, increasing comfort. Additionally, to increase comfort you can create electrode units without electrodes and the wires to place at various nodes around the frame. This will also help to distribute  pressure.

These are the pieces that comprise one full electrode unit:


First, slide a **Machine Screw (2-56 Thread, 3/4" Length)** through the FRI electrode and guide it into the ELECTRODE_HOLDER. For channel 1 and channel 2 you may use flat electrodes since these elctrodes will be on your forehead where there is no hair.



Then, slide the screw and electrode into the ELECTRODE_HOLDER


Next, twist a *Hex Nut (2-56 Thread Size, 3/16" Wide, 1/16" High)* onto the screw, securing the electrode to the holder.


Next, twist the exposed metal of your wire so that it is tight and clean.



This part is a little bit tricky! Wrap the exposed metal of your wire once around the remaining thread of the screw. You can use your finger nail to pinch the wire down against the nut, while wrapping. 




Then, twist your second Hex Nut onto the screw, securing the wire between the two nuts. You can use wire cutters to firmly screw the nut into place.



Slide a **Suggested Spring 1 (aka "Weak Spring")** and then the OCTABOLT around the wire as shown below.



Snap the full electrode unit together, guiding the semi-spherical protrusions on the outside of the SPRING_CASING into the relief cuts of the OCTABOLT. 



Voila! Spring-loaded electrode GIF!



### Insert electrode units into your Ultracortex

Once you've asesembled all of your electrode units, twist them into their respective Ultracortex frame nodes. If the parts are tough to twist into place by hand, use the OCTATOOL that comes with your kit as shown in the picture below. Over time the resistance between the OCTANUT and OCTABOLT will diminish, and the pieces will twist into place more easily.



### Reconnect wires to OpenBCI & connect ear clip electrodes (Reference & Ground)

Now that all of your electrode units are connected to your Ultracortex frame, reconnect the electrode wires to the OpenBCI board as detailed above. If you have some handy, you may want to use zip ties to secure the loose wiring to the Ultracortex frame. Later revisions of the headset will be designed to account for this. ;)



Next, connect two touch-proof adapter cables to SRB2 and bottom BIAS pin (white and black respectively in the image below). You can use the touch-proof adapter that comes with the OpenBCI 32bit Board or OpenBCI 16-channel R&D Kit. Then connect your [ear clip electrodes](http://fri-fl-shop.com/product/td-430-silver-disc-electrode-ear-clip/) to these touch-proof adapters. These ear clip electrodes serve as the reference and bias (ground with common-mode noise rejection) for your EEG system.

Alternatively, cut the earclip wire to about a foot long. Cut the touch-proof adapter wire to 2 inches long. Solder these two wires together, and shrink wrap them or wrap them in electrical tape.



For the 16 channel board, cut and solder two wires to the ear clip wire as shown:





### Fasten the BOARD_COVER

Now clip your board cover into place. If you've soldered any of the header rows onto your OpenBCI board, you'll need to use the BOARD_COVER_ADVANCED, as seen in the picture below. Otherwise, you can use the BOARD_COVER_STANDARD with the OpenBCI logo.



## Supernova Add-Ons

### Parts



To add the QUADSTAR extensions to your Supernova, use the following parts:

**3D Printed Parts**

**Note:** the QUAD_STAR should be printed in a stretchy filament (like NinjaFlex or SemiFlex), as listed above in the Suggested Print Settings section.

* [Quadstar](https://github.com/OpenBCI/Ultracortex/blob/master/Mark_III_Nova/STLs/MECH_PARTS/QUADSTAR.stl) (**8X**) -- [.STL download link](https://github.com/OpenBCI/Ultracortex/raw/master/Mark_III_Nova/STLs/MECH_PARTS/QUADSTAR.stl)
* [Octaring](https://github.com/OpenBCI/Ultracortex/blob/master/Mark_III_Nova/STLs/MECH_PARTS/OCTARING.stl) (**8X**) -- [.STL download link](https://github.com/OpenBCI/Ultracortex/raw/master/Mark_III_Nova/STLs/MECH_PARTS/OCTANUT.stl)

**Non-3D Printed Parts**

* Zip ties

### Stretch QUADSTAR over OCTARING

Take your QUADSTAR and stretch it so that it fits over the OCTARING



### Zip Tie QUADSTAR onto frame

Using zip ties, tie down the corners of the QUADSTAR onto the frame of your ULTRACORTEX. You should be using four zip ties per QUADSTAR. For QUADSTARS that are next to each other, re-use the same zip tie to tie them both down to the frame. NOTE: Tie the QUADSTARS down loosely at first in order to ensure that they are all centered while tied down to the frame. Once all of the QUADSTARS are tied loosely to the frame, tighten them to secure them to the frame.






### Cut Zip Ties

Turn the ULTRACORTEX over and snip off all of the loose ends of the zip ties.



### Insert Comfort Nodes

Next, screw a comfort node into each of the 8 QUADSTARS.



### Supernova Assembly Complete!


### Adjust the Ultracortex for your head

Put the Ultracortex Mark 3 onto your head and gradually tighten the electrode units until the electrodes are snuggly (but comfortably) against your scalp. If it is difficult to twist the OCTABOLT pieces by hand, you may need to use the OCTATOOL as seen in the gif below. 

**Be careful** not to strain the electrode wires when twisting the electrode unit with the OCTATOOL, or you may separate the wire from the electrode itself. Turn the OCTABOLT until the wire is nearly taught, then reposition the wire and tool and twist again, as demonstrated in the gif.



### Examine your brain waves!

Place your UltraCortex on your head so that the back center node is roughly the same distance above your inion (bump on the back of your skull) as the front center node is above the bridge of your nose. As you place the UltraCortex on your head, the springs should adjust to the shape and size of your head.

Now that you have your Ultracortex assembled and comfortably adjusted to your head size and shape, it's brain wave time!



Check out the [Getting Started w/ OpenBCI tutorial](http://docs.openbci.com/tutorials/01-GettingStarted) to get up-and-running with the [OpenBCI Processing GUI](https://github.com/OpenBCI/OpenBCI_Processing).

Below is a screenshot of what the GUI looks like when you've got your OpenBCI + Ultracortex (w/ 8 channels) hooked up! You can see a nice alpha (~11 hz) spike on the FFT Plot. 



### Give Us Feedback!

If you have questions, comments, or suggestions regarding the printing and/or assembly of the Ultracortex, we'd love to hear from you. Please submit issues to this repository or email us at [contact@openbci.com](mailto:contact@openbci.com). Or take some pictures of yourself wearing the Ultracortex and Tweet at us ([@OpenBCI](https://twitter.com/OpenBCI) & [@Ultracortex](https://twitter.com/Ultracortex))!

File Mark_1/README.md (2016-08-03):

# ultracortex

**Note:** Mark 1 has been depricated by the newer model [Mark III REVISED](https://github.com/OpenBCI/Ultracortex/tree/master/Mark_III_Nova_REVISED)

Files related to the ultracortex, the 3D-printable EEG headset compatible with OpenBCI (currently under development).

The electrodes seen in the photos here are dry electrodes from Florida Research Instruments (FRI), found here: http://fri-fl-shop.com/product/package-of-15-disposable-reusable-dry-electrodes-and-10-disposablereusable-eeg-cup-electrodes-and-5-leads-red-white-green-black-brown/

The FRI_electrode_mount.stl was modeled to serve as a mechanical mount for the FRI electrodes.

The screws and nuts used to fasten the FRI electrode to the FRI_electrode_mount are:

- screws: [#2-56 Brass (1/2" length")](http://www.mcmaster.com/#91802a081/=xd3x3s) for variations in head style, see [here](http://www.mcmaster.com/#machine-screws/=xd3ycd)
- nuts:  [#2-56 Brass](https://www.boltdepot.com/Product-Details.aspx?product=7210)
- ground clip to fasten between the nuts and solder the electrode to: [Solder Lug](http://www.digikey.com/product-search/en/connectors-interconnects/terminals-solder-lug-connectors/1442863)

### Image References















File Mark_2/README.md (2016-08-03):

# Ultracortex (Mark 2)

**Note:** Mark 2 has been depricated by the newer model [Mark III REVISED](https://github.com/OpenBCI/Ultracortex/tree/master/Mark_III_Nova_REVISED)



## Print Settings (verified)

* Printer used: Makerbot Rep 2
* Material: PLA

#### For M2-Frame Components

* Resolution: Low (Faster)
* Raft: Yes
* Supports: Yes (even though this uses A LOT of extra material)
* Infill: 100% (we want it sturdy)
* Number of shells: 3
* Layer Height: 0.3mm
* Temperature: 235 C
* Speed while Extruding: 45 mm/s (you may be able to increase this depending on how well tuned your 3D printer is)
* Speed while traveling: 150 mm/s

#### For M2-Electrode-Mount Components

* Resolution: Low (Faster)
* **Raft: No**
* **Supports: No**
* Infill: 100% (we want it sturdy)
* Number of shells: 3
* Layer Height: 0.3mm
* Temperature: 235 C
* Speed while Extruding: 45 mm/s (you may be able to increase this depending on how well tuned your 3D printer is)
* Speed while traveling: 150 mm/s

## Spring Options

We are in the process of testing different springs to be nested 

#### Spring 1 (tested)

[McMaster-Carr](http://www.mcmaster.com/#) > [1	9657K279	Steel Compression Spring, Zinc-Plated Music Wire, .500" L, .600" OD, .045" Wire, Packs of 12](http://www.mcmaster.com/#9657k279/=xkccgf)

**Summary**: The **~23 lb/in** is too strong!
 
#### Spring 2 (tested)

[centuryspring.com](http://centuryspring.com): Custom spring order of **Part # B6-8**

**Summary:** custom order... **~1 lb/in** is too weak...

#### Spring 3 & 4 (untested, but potentially better)

Our working version of the headset uses Springs 1 & 2, but I would recommend trying the following instead:

- [NN-92 - 2.4 lb/in](http://www.centuryspring.com/Store/item_detail.php?StockNumber=NN-92)
- [12685 - 3.9 lb/in](http://www.centuryspring.com/Store/item_detail.php?StockNumber=12685)

## Electrodes

Dry (spikey) electrodes to be installed in Ultracortex nodes with hair: 

* [Disposable / Reusable Dry EEG Electrode ($0.60 each at 50+ quantity purchase) ](http://fri-fl-shop.com/product/tde-200/)

Dry (non-spikey) electrodes to be installed in Ultracortex nodes without hair (forehead, for instance): 

* [Disposable / Reusable Cup Wet/Dry EEG Electrode ($10.00 for 15) ](http://fri-fl-shop.com/product/disposable-reusable-dry-eeg-electrode-quantity-of-15-tde-200a1/)

Ear Clip electrode (for reference)

* [TDI-430 Silver-Silver Chloride Ear Clip Electrode ($19.95 each)](http://fri-fl-shop.com/product/td-430-silver-disc-electrode-ear-clip/)

## Nuts & Bolts for Connecting Electrodes

We use small stainless steel screws and hex nuts to fasten the FRI electrodes (listed above) to the 3D-printed electrode mount components &  wiring that connects the electrodes back to the OpenBCI board. We used stripped [Electrode Starter Kit (ESK)](https://openbci.myshopify.com/collections/frontpage/products/openbci-electrode-starter-kit) electrodes as the cabling, by removing the gold cup with a wire cutter and looping the exposed wire around the screw between the two tightened hex nuts (as seen in the picture below).

* [Stainless Steel Pan Head Phillips Machine Screw, 2-56 Thread, 3/8" Length ($5.70 per pack of 50)](http://www.mcmaster.com/#91735a017/=xzahfj)
* [Stainless Steel Hex Nut, 2-56 Thread Size, 3/16" Wide, 1/16" High](http://www.mcmaster.com/#91841a003/=xzahv0)



## Other Helpful Information

*  The following equipment/accessories were either necessary or very helpful in the assembly of this headset.
	* super glue
	* sandpaper
	* coarse flat & circular files
	* some sort of flexible wiring (terminating in a female header) to connect the electrodes back to the 
	* OpenBCI board. We used stripped [ESK](https://openbci.myshopify.com/collections/frontpage/products/	openbci-electrode-starter-kit) electrodes & stripped touch-proof connector cabling from the [OpenBCI Board Kit](https://openbci.myshopify.com/collections/frontpage/products/openbci-8-bit-board-kit).
	* an exacto/razor blade
	* wirecutters
	* needle-nose pliers
	

	
* The "M2_Electrode Mount A_01" part has a small lip on the inside (where the spring fits into) that must be manually removed with an exacto/razor blade. 
* Most of the tolerances between pieces are too tight, so assembly requires substantial filing and sanding.
* The "M2_Electrode Spacer_01" part is used to adjust for different head shapes and sizes
* With this versoin (M2) we unfortunately only have one frame size, so this headset will not fit most heads, even with the spacers and springs.
* Before printing, make sure to re-orient the frame STLs so the flat sides of the model are on the platform.

## Photos of Ultracortex M2












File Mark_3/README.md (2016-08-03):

#Ultracortex Mark 3
*Development Period: July 2015 — September 2015*

**Note:** Mark III has been depricated by the newer model [Mark III REVISED](https://github.com/OpenBCI/Ultracortex/tree/master/Mark_III_Nova_REVISED)



####Complete Ultracortex Mark 3 kits are [available for sale](http://openbci.myshopify.com/collections/frontpage/products/ultracortex-mark-3-eeg-headset-kit-assembly-required) in the OpenBCI Online Store!

The Ultracortex is an open-source, 3D-printable headset intended to work with the [OpenBCI system](http://openbci.com/). It is capable of recording research-grade brain activity (EEG), muscle activity (EMG), and heart activity (ECG). The Ultracortex is under constant iteration. If you print/assemble your own Ultracortex, we would love to hear your feedback. Send us an email at [contact@openbci.com](mailto:contact@openbci.com) or Tweet at us ([@Ultracortex](https://twitter.com/Ultracortex) & [@OpenBCI](https://twitter.com/OpenBCI))!

Designers & Engineers:

* [Aaron Trocola (aka Threeform)](http://threeformfashion.com/)
* [Conor Russomanno](https://twitter.com/russomanno15)
* [Joel Murphy (aka SafeForRobots)](https://twitter.com/safeforrobots)

## THE COMPLETE ULTRACORTEX

**Note:** the part quantities listed below assume you are making an electrode holder for all 21 nodes of the Ultracortex Mark 3. In reality, you will likely have only 8 or 16 electrodes, depending on whether you are working with the [OpenBCI 32bit Board](http://openbci.myshopify.com/collections/frontpage/products/openbci-32-bit-board-kit) (8 channels) or the [OpenBCI 16-channel R&D Kit](http://openbci.myshopify.com/collections/frontpage/products/openbci-16-channel-r-d-kit) (16 channels). You may only want to create as many electrode units as you have channels, and then add more as necessary. In general, more electrodes will distribute the downward scalp pressure, increasing comfort.

###3D-printed Parts:

* [FRAME](https://github.com/OpenBCI/Ultracortex/tree/master/Mark_3/STLs/FRAME) (head circumference: small = 50-55cm, medium = 55-60cm, large = 60-65cm)
	* FRAME_FRONT (**x1**) — .STLs ([small](https://github.com/OpenBCI/Ultracortex/raw/master/Mark_3/STLs/FRAME/small/FRONT_small.stl) / [medium](https://github.com/OpenBCI/Ultracortex/raw/master/Mark_3/STLs/FRAME/medium/FRONT_medium.stl) / [large](https://github.com/OpenBCI/Ultracortex/raw/master/Mark_3/STLs/FRAME/large/FRONT_large.stl))
	* FRAME_BACK (**x1**) — .STLs ([small](https://github.com/OpenBCI/Ultracortex/raw/master/Mark_3/STLs/FRAME/small/BACK_small.stl) / [medium](https://github.com/OpenBCI/Ultracortex/raw/master/Mark_3/STLs/FRAME/medium/BACK_medium.stl) / [large](https://github.com/OpenBCI/Ultracortex/raw/master/Mark_3/STLs/FRAME/large/BACK_large.stl))
* [MECH_PARTS](https://github.com/OpenBCI/Ultracortex/tree/master/Mark_3/STLs/MECH_PARTS)
	* [OCTANUT](https://github.com/OpenBCI/Ultracortex/blob/master/Mark_3/STLs/MECH_PARTS/OCTANUT.stl) (**x21**) — [.STL download link](https://github.com/OpenBCI/Ultracortex/raw/master/Mark_3/STLs/MECH_PARTS/OCTANUT.stl)
	* [OCTABOLT](https://github.com/OpenBCI/Ultracortex/blob/master/Mark_3/STLs/MECH_PARTS/OCTABOLT.stl) (**x21**) — [.STL download link](https://github.com/OpenBCI/Ultracortex/raw/master/Mark_3/STLs/MECH_PARTS/OCTABOLT.stl)
	* [SPRING_CASING](https://github.com/OpenBCI/Ultracortex/blob/master/Mark_3/STLs/MECH_PARTS/SPRING_CASING.stl) (**x21**) — [.STL download link](https://github.com/OpenBCI/Ultracortex/raw/master/Mark_3/STLs/MECH_PARTS/SPRING_CASING.stl)
	* [ELECTRODE_HOLDER](https://github.com/OpenBCI/Ultracortex/blob/master/Mark_3/STLs/MECH_PARTS/ELECTRODE_HOLDER.stl) (**x21**) — [.STL download link](https://github.com/OpenBCI/Ultracortex/raw/master/Mark_3/STLs/MECH_PARTS/ELECTRODE_HOLDER.stl)
* [BOARD_HOLDER](https://github.com/OpenBCI/Ultracortex/blob/master/Mark_3/STLs/BOARD_HOLDER.stl) (**x1**) — [.STL download link](https://github.com/OpenBCI/Ultracortex/raw/master/Mark_3/STLs/HOLDER_AND_COVER/BOARD_HOLDER.stl)
* BOARD_COVER (**x1**) — choose STANDARD or ADVANCED
	* [STANDARD](https://github.com/OpenBCI/Ultracortex/blob/master/Mark_3/STLs/BOARD_COVER_logo.stl) — [.STL download link](https://github.com/OpenBCI/Ultracortex/raw/master/Mark_3/STLs/HOLDER_AND_COVER/BOARD_COVER_STANDARD.stl)
	* [ADVANCED](https://github.com/OpenBCI/Ultracortex/blob/master/Mark_3/STLs/BOARD_COVER_advancedVersion.stl) (for extra hardware accessibility / if you've soldered on your header rows) — [.STL download link](https://github.com/OpenBCI/Ultracortex/raw/master/Mark_3/STLs/HOLDER_AND_COVER/BOARD_COVER_ADVANCED.stl)

###Non-printed Parts:
 	
* Additional Hardware:
	* **Suggested Spring 1** listed below (**x21**)
	* **Suggested Spring 2** listed below (**x5**)
	* **Suggested Nuts** listed below (**x42**)
	* **Suggested Bolts** listed below (**x21**)
	* 1/4" #4 Drive Screw listed below (**x8**) for mounting the BOARD_HOLDER and OpenBCI Board
* Wiring (**x21**)
	* We strip apart the [Gold Cup Electrodes](http://openbci.myshopify.com/collections/frontpage/products/openbci-gold-cup-electrodes) or from the Touch-Proof Connector cable that comes with an [OpenBCI 32bit Board Kit](http://openbci.myshopify.com/collections/frontpage/products/openbci-32-bit-board-kit).
* Dry electrodes by Florida Research Instruments
	* (**18x**) Dry (spikey) electrodes to be installed in Ultracortex nodes with hair: [Disposable / Reusable Dry EEG Electrode ($0.60 each at 50+ quantity purchase) ](http://fri-fl-shop.com/product/tde-200/)
	* (**3x**) Dry (non-spikey) electrodes to be installed in Ultracortex nodes without hair (forehead, for instance): [Disposable / Reusable Cup Wet/Dry EEG Electrode ($10.00 for 15) ](http://fri-fl-shop.com/product/disposable-reusable-dry-eeg-electrode-quantity-of-15-tde-200a1/)
	* (**2x**) Ear Clip electrode (for reference): [TDI-430 Silver-Silver Chloride Ear Clip Electrode ($19.95 each)](http://fri-fl-shop.com/product/td-430-silver-disc-electrode-ear-clip/)
* (**1x**) An [OpenBCI 32bit Board](http://openbci.myshopify.com/collections/frontpage/products/openbci-32-bit-board-kit) or an [OpenBCI 16-channel R&D Kit](http://openbci.myshopify.com/collections/frontpage/products/openbci-16-channel-r-d-kit)
* (**1x**) Lithium Ion Rechargeable Battery Pack (~500mAh) — [Sparkfun](https://www.sparkfun.com/products/10718) or [Adafruit](http://www.adafruit.com/products/1578)
* (**1x**) [A charger for your battery pack](https://www.adafruit.com/products/1304)
* (**~10x**) [Zip tie](http://www.amazon.com/Black-Zip-Tie-100-Bag/dp/B0001IMMJI)

## THE COMPLETE ULTRACORTEX (w/ PICTURES)

###3D-printed Parts:

####(1x) FRAME

* [FRAME](https://github.com/OpenBCI/Ultracortex/tree/master/Mark_3/STLs/FRAME) (head circumference: small = 50-55cm, medium = 55-60cm, large = 60-65cm)
	* FRAME_FRONT (**x1**) — .STLs ([small](https://github.com/OpenBCI/Ultracortex/raw/master/Mark_3/STLs/FRAME/small/FRONT_small.stl) / [medium](https://github.com/OpenBCI/Ultracortex/raw/master/Mark_3/STLs/FRAME/medium/FRONT_medium.stl) / [large](https://github.com/OpenBCI/Ultracortex/raw/master/Mark_3/STLs/FRAME/large/FRONT_large.stl))
	* FRAME_BACK (**x1**) — .STLs ([small](https://github.com/OpenBCI/Ultracortex/raw/master/Mark_3/STLs/FRAME/small/BACK_small.stl) / [medium](https://github.com/OpenBCI/Ultracortex/raw/master/Mark_3/STLs/FRAME/medium/BACK_medium.stl) / [large](https://github.com/OpenBCI/Ultracortex/raw/master/Mark_3/STLs/FRAME/large/BACK_large.stl))

 

####(21x) MECH_PARTS

* [MECH_PARTS](https://github.com/OpenBCI/Ultracortex/tree/master/Mark_3/STLs/MECH_PARTS)
	* [OCTANUT](https://github.com/OpenBCI/Ultracortex/blob/master/Mark_3/STLs/MECH_PARTS/OCTANUT.stl) (**x21**) — [.STL download link](https://github.com/OpenBCI/Ultracortex/raw/master/Mark_3/STLs/MECH_PARTS/OCTANUT.stl)
	* [OCTABOLT](https://github.com/OpenBCI/Ultracortex/blob/master/Mark_3/STLs/MECH_PARTS/OCTABOLT.stl) (**x21**) — [.STL download link](https://github.com/OpenBCI/Ultracortex/raw/master/Mark_3/STLs/MECH_PARTS/OCTABOLT.stl)
	* [SPRING_CASING](https://github.com/OpenBCI/Ultracortex/blob/master/Mark_3/STLs/MECH_PARTS/SPRING_CASING.stl) (**x21**) — [.STL download link](https://github.com/OpenBCI/Ultracortex/raw/master/Mark_3/STLs/MECH_PARTS/SPRING_CASING.stl)
	* [ELECTRODE_HOLDER](https://github.com/OpenBCI/Ultracortex/blob/master/Mark_3/STLs/MECH_PARTS/ELECTRODE_HOLDER.stl) (**x21**) — [.STL download link](https://github.com/OpenBCI/Ultracortex/raw/master/Mark_3/STLs/MECH_PARTS/ELECTRODE_HOLDER.stl)

 

####(1x) BOARD_HOLDER

* [BOARD_HOLDER](https://github.com/OpenBCI/Ultracortex/blob/master/Mark_3/STLs/BOARD_HOLDER.stl) (**x1**) — [.STL download link](https://github.com/OpenBCI/Ultracortex/raw/master/Mark_3/STLs/BOARD_HOLDER.stl)

 

####(1x) BOARD_COVER

* BOARD_COVER (**x1**) — choose STANDARD or ADVANCED
	* [STANDARD](https://github.com/OpenBCI/Ultracortex/blob/master/Mark_3/STLs/BOARD_COVER_logo.stl) — [.STL download link](https://github.com/OpenBCI/Ultracortex/raw/master/Mark_3/STLs/BOARD_COVER_logo.stl)
	* [ADVANCED](https://github.com/OpenBCI/Ultracortex/blob/master/Mark_3/STLs/BOARD_COVER_advancedVersion.stl) (for extra hardware accessibility / if you've soldered on your header rows) — [.STL download link](https://github.com/OpenBCI/Ultracortex/raw/master/Mark_3/STLs/BOARD_COVER_advancedVersion.stl)

 



###Non-printed Parts:

####Suggested springs: 

* Suggested Spring 1 (**x21**) — aka "Weak Spring" — [Century Spring Corp. Stock #: U-4](http://cad.centuryspring.com/db/service?domain=century&command=showProduct&category=compression&product=U-4) — this spring is not as strong as spring 2. We use it to mount the electrodes. The low "Rate" (1.3 lbs/in) makes it more forgiving and comfortable when holding the spikey electrode against your head. This process is described in more detail below (in the "Assembly Instructions" section).



* Suggested Spring 2 (**x5**) — aka "Strong Spring" — [Century Spring Corp. Stock #: S-845](http://cad.centuryspring.com/db/service?domain=century&command=showProduct&category=compression&product=S-845) — this spring has a much stronger "Rate" (14 lb/in). This makes is ideal to act as a standoff at locations where you do not have a spikey electrode. This process is described in more detail below (in the "Assembly Instructions" section).



####Suggested nuts/bolts:

We use small stainless steel screws and hex nuts to fasten the FRI electrodes (listed above) to the 3D-printed electrode mount components &  wiring that connects the electrodes back to the OpenBCI board. We used stripped [Gold Cup Electrodes](http://openbci.myshopify.com/collections/frontpage/products/openbci-gold-cup-electrodes) as the cabling, by removing the gold cup with a wire cutter and looping the exposed wire around the screw between the two tightened hex nuts (as seen in the picture below).

* (**21x**) [Stainless Steel Pan Head Phillips Machine Screw, 2-56 Thread, 3/8" Length ($5.70 per pack of 50)](http://www.mcmaster.com/#91735a017/=xzahfj)
* (**42x**) [Stainless Steel Hex Nut, 2-56 Thread Size, 3/16" Wide, 1/16" High](http://www.mcmaster.com/#91841a003/=xzahv0)



####Suggested screws for fastening BOARD_MOUNT & OpenBCI Board

* (**8x**) [#4 Drive Screw](http://www.mcmaster.com/#90077a106/=yysd5f)



####Wiring

* (**21x**) We strip apart the [Gold Cup Electrodes](http://openbci.myshopify.com/collections/frontpage/products/openbci-gold-cup-electrodes)) or the Touch-Proof Connector cable that comes with an [OpenBCI 32bit Board Kit](http://openbci.myshopify.com/collections/frontpage/products/openbci-32-bit-board-kit).



####Dry electrodes by Florida Research Instruments

* (**18x**) Dry (spikey) electrodes to be installed in Ultracortex nodes with hair: [Disposable / Reusable Dry EEG Electrode ($0.60 each at 50+ quantity purchase) ](http://fri-fl-shop.com/product/tde-200/)
* (**3x**) Dry (non-spikey) electrodes to be installed in Ultracortex nodes without hair (forehead, for instance): [Disposable / Reusable Cup Wet/Dry EEG Electrode ($10.00 for 15) ](http://fri-fl-shop.com/product/disposable-reusable-dry-eeg-electrode-quantity-of-15-tde-200a1/)
* (**2x**) Ear Clip electrode (for reference): [TDI-430 Silver-Silver Chloride Ear Clip Electrode ($19.95 each)](http://fri-fl-shop.com/product/td-430-silver-disc-electrode-ear-clip/)



####(1x) An [OpenBCI 32bit Board](http://openbci.myshopify.com/collections/frontpage/products/openbci-32-bit-board-kit) (8 electrode channels) or an [OpenBCI 16-channel R&D Kit](http://openbci.myshopify.com/collections/frontpage/products/openbci-16-channel-r-d-kit) (16 electrode channels)



####(**1x**) ~500mAh lithium ion rechargeable battery pack ([Sparkfun](https://www.sparkfun.com/products/10718) or [Adafruit](http://www.adafruit.com/products/1578)) & (**1x**) [A charger for your battery pack](https://www.adafruit.com/products/1304)



#### (**~10x**) [Zip tie](http://www.amazon.com/Black-Zip-Tie-100-Bag/dp/B0001IMMJI)



## SUGGESTED PRINT SETTINGS

* FRAME_FRONT & FRAME_BACK
	* Material: PLA
	* Supports: YES
	* Raft: hopefully NO (but if supports aren't sticking, try the raft)
	* Infill: 20%
	* Layer Height: 0.2mm
	* Number of Shells: 3
	* Speed while extruding: 50-70% (slow it down if possible; these parts are detailed)
* MECH_PARTS (OCTANUT / BOLT / SPRING_CASING / ELECTRODE_HOLDER)
	* Material: PLA
	* Supports: NO
	* Raft: NO
	* Infill: 20%
	* Layer Height: 0.2mm
	* Number of Shells: 3
	* Speed while extruding: 50-70% (slow it down if possible; these parts are detailed)
* BOARD_MOUNT, BOARD_COVER_STANDARD, & BOARD_COVER_ADVANCED
	* Material: PLA
	* Supports: NO
	* Raft: NO
	* Infill: 20%
	* Layer Height: 0.2mm
	* Number of Shells: 3
	* Speed while extruding: 50-70% (slow it down if possible; these parts are detailed)

## RECOMMENDED ASSEMBLY TOOLS

1. [Loctite Super Glue w/ Cyanoacrylate](http://www.amazon.com/Loctite-1365882-20-Gram-Bottle-Professional/dp/B004Y960MU/ref=sr_1_1?s=automotive&ie=UTF8&qid=1440204266&sr=1-1&keywords=loctite+cyanoacrylate&pebp=1440204267936&perid=0HJQ0FB9G4J9SEBQBVGA)
2. coarse flat & circular files (for removing support artifacts)
3. medium sand paper
4. exacto blade
5. philips head screw driver
6. wire cutters
7. needle-nose pliers
8. snippers



## ASSEMBLY INSTRUCTIONS

### Remove residual support material & print flaws

Use sand paper, a file, and snippers to clean your FRAME and other 3D-printed parts. The most important part of this process is that you thoroughly clean out the frames nodes where you will place your OCTANUT pieces.




### Glue the FRAME together

Carefully, glue the FRAME_FRONT and FRAME_BACK together with your Cyanoacrylate super glue. The best way to do this is to place both halves of the frame on a level surface and carefully bring them together. Be sure to be precise; it's VERY difficult to pull the pieces apart once you've put them together.



### Mount the OpenBCI BOARD_HOLDER

Use four #4 Drive Screws to mount the BOARD_HOLDER to the FRAME. Make sure that the orientation of the BOARD_HOLDER matches that of the pictures below:




### Insert OCTANUT pieces (x21) into frame

**Note:** at each node, you must line up the cut in the OCTANUT with the indentation on the frame as indicated in the picture below.



Your Ultracortex should now look like this:



### Embed OpenBCI into the Ultracortex

Connect your ~500 mAh lithium ion rechargeable batter to the back of your 32bit OpenBCI Board. Then fold the battery and its wires neatly behind the board before inserting the board into the BOARD_MOUNT. You can then use one of your #4 Drive Screws to secure the OpenBCI Board to the BOARD_MOUNT. Typically you don't need to use any #4 Drive Screws because the BOARD_COVER locks the OpenBCI Board in place, but in this case it's a good idea because you'll want to see where you're connecting your wires.



### Identify electrode locations

Before creating your electrode mounts, it's a good idea to think about where you may want to place the electrodes on the Ultracortex FRAME. The placement of the electrode may affect how long you make the wire between the electrode and where the OpenBCI is mounted, at the back of the frame.

The Ultracortex node locations are based on the [10-20 system](https://goo.gl/gSwYw), which is the internationally accepted standard for electrode placement in the context of EEG.

The images below indicates the default 10-20 electrode locations that the OpenBCI Graphical User Interface expects. This application is great for viewing/recording your EEG and can be found in our [OpenBCI_Processing](http://) repo. The blue nodes indicate the 8 default 10-20 locations (channels 1-8) of the 32bit Board. The red nodes indicate the default 10-20 locations of channels 9-16 when using the OpenBCI 16-channel R&D Kit. 

For the remainder of this tutorial, the blue nodes on the 10-20 system diagram (channels 1-8 of the OpenBCI default settings) will be used. The channel to 10-20 system correlations are as follows:

* Channel 1 - Fp1
* Channel 2 - Fp2
* Channel 3 - C3
* Channel 4 - C4
* Channel 5 - P7
* Channel 6 - P8
* Channel 7 - O1
* Channel 8 - O2



### Connect wiring to OpenBCI

Before shortening any of your wires, connect the female header of each wire to the N pin of channels 1-8, as indicated in the image to the lower right. The N pins are the ones closer to the OpenBCI Board. By default, the OpenBCI Board references these 8 pins with the SRB 2 pin (the bottom SRB pin).



### Measure, cut, and strip wires

For each wire, measure the distance between where it is connected to the OpenBCI Board and the node that it will terminate at on the Ultracortex frame. Give yourself 2-3 inches of slack (extra length), because you're going to strip the end of the wire, and you may want the extra slack to zip-tie/tape the wiring to the frame later on.

As mentioned above, if you're using the default OpenBCI electrode configuration, cut the wires so that they terminate at the following nodes:

* Channel 1 - Fp1
* Channel 2 - Fp2
* Channel 3 - C3
* Channel 4 - C4
* Channel 5 - P7
* Channel 6 - P8
* Channel 7 - O1
* Channel 8 - O2

After you're done measuring, cutting, and stripping your wires, disconnect them from the OpenBCI board. You will need the female header free so you can guide the springs and OCTANUT pieces into place in the following step. But remember which wire goes where!



### Assemble electrode mounts (x8 or x16)
**Note:** repeat the following steps as many times as necessary, depending upon your OpenBCI setup. In general, using more electrodes will distribute the downward scalp pressure, increasing comfort. Additionally, to increase comfort you can create electrode units without electrodes and the wires to place at various nodes around the frame. This will also help to distribute  pressure.

These are the pieces that comprise one full electrode unit:


First, slide a **Machine Screw (2-56 Thread, 3/8" Length)** through the FRI electrode and guide it into the ELECTRODE_HOLDER.


Then, twist your first **Hex Nut (2-56 Thread Size, 3/16" Wide, 1/16" High)** onto the screw, securing the electrode to the holder.


Next, twist the exposed metal of your wire so that it is tight and clean.


This part is a little bit tricky! Wrap the exposed metal of your wire around the remaining thread of the screw. You can use your finger nail to pinch the wire down against the nut, while wrapping.


Then, twist your second Hex Nut onto the screw, securing the wire between the two nuts. You can use wire cutters to firmly screw the nut into place.


Slip the SPRING_CASING around the wire, as shown below:


Put a thin line of super glue on the outer edge of the top of the ELECTRODE_HOLDER.


Press the SPRING_CASING against the ELECTRODE_HOLDER and hold for a few seconds to make sure the two pieces are securely connected.


Now sand around the seam between the ELECTRODE_HOLDER and SPRING_CASING. Try your best to make the full cylinder as smooth as possible. Take your time ensuring that the cylinder is as smooth as you can make it, since this will You don't want it to catch on the inside of the OCTABOLT.


Slide a **Suggested Spring 1 (aka "Weak Spring")** and then the OCTABOLT around the wire as shown below.


Snap the full electrode unit together, guiding the semi-spherical protrusions on the outside of the SPRING_CASING into the relief cuts of the OCTABOLT. 


Voila! Spring-loaded electrode GIF!



### Insert electrode units into your Ultracortex

Once you've asesembled all of your electrode units, twist them into their respective Ultracortex frame nodes. If the parts are tough to twist into place by hand, use the OCTATOOL that comes with your kit as shown in the picture below. Over time the resistance between the OCTANUT and OCTABOLT will diminish, and the pieces will twist into place more easily.



### Reconnect wires to OpenBCI & connect ear clip electrodes (Reference & Ground)

Now that all of your electrode units are connected to your Ultracortex frame, reconnect the electrode wires to the OpenBCI board as detailed above. If you have some handy, you may want to use zip ties to secure the loose wiring to the Ultracortex frame. Later revisions of the headset will be designed to account for this. ;)



Next, connect two touch-proof adapter cables to SRB2 and bottom BIAS pin (white and black respectively in the image below). You can use the touch-proof adapter that comes with the OpenBCI 32bit Board or OpenBCI 16-channel R&D Kit. Then connect your [ear clip electrodes](http://fri-fl-shop.com/product/td-430-silver-disc-electrode-ear-clip/) to these touch-proof adapters. These ear clip electrodes serve as the reference and bias (ground with common-mode noise rejection) for your EEG system.



### Fasten the BOARD_COVER

Now clip your board cover into place. If you've soldered any of the header rows onto your OpenBCI board, you'll need to use the BOARD_COVER_ADVANCED, as seen in the picture below. Otherwise, you can use the BOARD_COVER_STANDARD with the OpenBCI logo.



### Adjust the Ultracortex for your head

Put the Ultracortex Mark 3 onto your head and gradually tighten the electrode units until the electrodes are snuggly (but comfortably) against your scalp. If it is difficult to twist the OCTABOLT pieces by hand, you may need to use the OCTATOOL as seen in the gif below. 

**Be careful** not to strain the electrode wires when twisting the electrode unit with the OCTATOOL, or you may separate the wire from the electrode itself. Turn the OCTABOLT until the wire is nearly taught, then reposition the wire and tool and twist again, as demonstrated in the gif.



### Improve Comfort!

To make the headset substantially more comfortable, assemble a few Electrode Units without a "spikey" electrode or any of the cabling as shown in the picture below. For this, **use the Suggested Spring 2 (aka "Strong Spring").**




Then insert these spring-loaded standoffs along the midline of the headset and at other locations of your choosing (as indicated by the green circles in the image below). This will redistribute the weight of the headset, relieving the majority of the pressure at the "spikey" electrode locations.



### Examine your brain waves!

Place your UltraCortex on your head so that the back center node is roughly the same distance above your inion (bump on the back of your skull) as the front center node is above the bridge of your nose. As you place the UltraCortex on your head, the springs should adjust to the shape and size of your head. If they get stuck, remove the nodes and sand them down further so that they smoothly adjust to your head size.

Now that you have your Ultracortex assembled and comfortably adjusted to your head size and shape, it's brain wave time!



Check out the [Getting Started w/ OpenBCI tutorial](http://docs.openbci.com/tutorials/01-GettingStarted) to get up-and-running with the [OpenBCI Processing GUI](https://github.com/OpenBCI/OpenBCI_Processing).

Below is a screenshot of what the GUI looks like when you've got your OpenBCI + Ultracortex (w/ 8 channels) hooked up! You can see a nice alpha (~11 hz) spike on the FFT Plot. 



### Give Us Feedback!

If you have questions, comments, or suggestions regarding the printing and/or assembly of the Ultracortex, we'd love to hear from you. Please submit issues to this repository or email us at [contact@openbci.com](mailto:contact@openbci.com). Or take some pictures of yourself wearing the Ultracortex and Tweet at us ([@OpenBCI](https://twitter.com/OpenBCI) & [@Ultracortex](https://twitter.com/Ultracortex))!

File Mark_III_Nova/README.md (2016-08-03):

#Ultracortex Mark III "Nova" & "Supernova"
*Development Period: February 2016 — April 2016*

**Note:** Mark III Nova & Super Nova has been depricated by the newer model [Mark III REVISED](https://github.com/OpenBCI/Ultracortex/tree/master/Mark_III_Nova_REVISED)



####Complete Ultracortex Mark 3 kits are [available for sale](http://openbci.myshopify.com/collections/frontpage/products/ultracortex-mark-3-eeg-headset-kit-assembly-required) in the OpenBCI Online Store!

The Ultracortex is an open-source, 3D-printable headset intended to work with the [OpenBCI system](http://openbci.com/). It is capable of recording research-grade brain activity (EEG), muscle activity (EMG), and heart activity (ECG). The Ultracortex is under constant iteration. If you print/assemble your own Ultracortex, we would love to hear your feedback. Send us an email at [contact@openbci.com](mailto:contact@openbci.com) or Tweet at us ([@Ultracortex](https://twitter.com/Ultracortex) & [@OpenBCI](https://twitter.com/OpenBCI))!

Designers & Engineers:

* [Aaron Trocola (aka Threeform)](http://threeformfashion.com/)
* [Conor Russomanno](https://twitter.com/russomanno15)
* [Joel Murphy (aka SafeForRobots)](https://twitter.com/safeforrobots)

## THE COMPLETE ULTRACORTEX

**Note:** the part quantities listed below assume you are making an electrode holder for all 21 nodes of the Ultracortex Mark 3. In reality, you will likely have only 8 or 16 electrodes, depending on whether you are working with the [OpenBCI 32bit Board](http://openbci.myshopify.com/collections/frontpage/products/openbci-32-bit-board-kit) (8 channels) or the [OpenBCI 16-channel R&D Kit](http://openbci.myshopify.com/collections/frontpage/products/openbci-16-channel-r-d-kit) (16 channels). You may only want to create as many electrode units as you have channels, and then add more as necessary. In general, more electrodes will distribute the downward scalp pressure, increasing comfort.

###3D-printed Parts:

* [FRAME](https://github.com/OpenBCI/Ultracortex/tree/master/Mark_III_Nova/STLs/FRAME) (head circumference: small = 50-55cm, medium = 55-60cm, large = 60-65cm)
	* FRAME_FRONT (**x1**) — .STLs ([small](https://github.com/OpenBCI/Ultracortex/raw/master/Mark_III_Nova/STLs/FRAME/small/FRAME_FRONT_small.stl) / [medium](https://github.com/OpenBCI/Ultracortex/raw/master/Mark_III_Nova/STLs/FRAME/medium/FRAME_FRONT_medium.stl) / [large](https://github.com/OpenBCI/Ultracortex/raw/master/Mark_III_Nova/STLs/FRAME/large/FRAME_FRONT_large.stl))
	* FRAME_BACK (**x1**) — .STLs ([small](https://github.com/OpenBCI/Ultracortex/raw/master/Mark_III_Nova/STLs/FRAME/small/FRAME_BACK_small.stl) / [medium](https://github.com/OpenBCI/Ultracortex/raw/master/Mark_III_Nova/STLs/FRAME/medium/FRAME_BACK_medium.stl) / [large](https://github.com/OpenBCI/Ultracortex/raw/master/Mark_III_Nova/STLs/FRAME/large/FRAME_BACK_large.stl))
* [MECH_PARTS](https://github.com/OpenBCI/Ultracortex/tree/master/Mark_III_Nova/STLs/MECH_PARTS)
	* [OCTANUT](https://github.com/OpenBCI/Ultracortex/blob/master/Mark_III_Nova/STLs/MECH_PARTS/OCTANUT.stl) (**x21**) — [.STL download link](https://github.com/OpenBCI/Ultracortex/raw/master/Mark_III_Nova/STLs/MECH_PARTS/OCTANUT.stl)
	* [OCTABOLT](https://github.com/OpenBCI/Ultracortex/blob/master/Mark_III_Nova/STLs/MECH_PARTS/OCTABOLT.stl) (**x21**) — [.STL download link](https://github.com/OpenBCI/Ultracortex/raw/master/Mark_III_Nova/STLs/MECH_PARTS/OCTABOLT.stl)
	* [OCTARING](https://github.com/OpenBCI/Ultracortex/blob/master/Mark_III_Nova/STLs/MECH_PARTS/OCTARING.stl) (**x21**) — [.STL download link](https://github.com/OpenBCI/Ultracortex/raw/master/Mark_III_Nova/STLs/MECH_PARTS/OCTARING.stl)
	* [ELECTRODE_HOLDER](https://github.com/OpenBCI/Ultracortex/blob/master/Mark_III_Nova/STLs/MECH_PARTS/E_HOLDER.stl) (**x21**) — [.STL download link](https://github.com/OpenBCI/Ultracortex/raw/master/Mark_III_Nova/STLs/MECH_PARTS/E_HOLDER.stl)
	* [QUADSTAR](https://github.com/OpenBCI/Ultracortex/blob/master/Mark_III_Nova/STLs/MECH_PARTS/QUADSTAR.stl) (**x21**) — [.STL download link](https://github.com/OpenBCI/Ultracortex/raw/master/Mark_III_Nova/STLs/MECH_PARTS/QUADSTAR.stl)
	* [Comfy Insert](https://github.com/OpenBCI/Ultracortex/blob/master/Mark_III_Nova/STLs/MECH_PARTS/Comfy_Insert.stl) (**x21**) — [.STL download link](https://github.com/OpenBCI/Ultracortex/raw/master/Mark_III_Nova/STLs/MECH_PARTS/Comfy_Insert.stl)	
* [BOARD_HOLDER](https://github.com/OpenBCI/Ultracortex/blob/master/Mark_III_Nova/STLs/HOLDER_AND_COVER/BOARD_HOLDER.stl) (**x1**) — [.STL download link](https://github.com/OpenBCI/Ultracortex/raw/master/Mark_III_Nova/STLs/HOLDER_AND_COVER/BOARD_HOLDER.stl)
* BOARD_COVER (**x1**) — choose STANDARD or ADVANCED
	* [STANDARD](https://github.com/OpenBCI/Ultracortex/blob/master/Mark_III_Nova/STLs/HOLDER_AND_COVER/BOARD_COVER_STANDARD.stl) — [.STL download link](https://github.com/OpenBCI/Ultracortex/raw/master/Mark_III_Nova/STLs/HOLDER_AND_COVER/BOARD_COVER_STANDARD.stl)
	* [HOLDER](https://github.com/OpenBCI/Ultracortex/blob/master/Mark_III_Nova/STLs/HOLDER_AND_COVER/BOARD_COVER_STANDARD.stl) — [.STL download link](https://github.com/OpenBCI/Ultracortex/raw/master/Mark_III_Nova/STLs/HOLDER_AND_COVER/BOARD_COVER_STANDARD.stl)	
	* [ADVANCED](https://github.com/OpenBCI/Ultracortex/blob/master/Mark_III_Nova/STLs/HOLDER_AND_COVER/BOARD_COVER_ADVANCED.stl) (for extra hardware accessibility / if you've soldered on your header rows) — [.STL download link](https://github.com/OpenBCI/Ultracortex/raw/master/Mark_III_Nova/STLs/HOLDER_AND_COVER/BOARD_COVER_ADVANCED.stl)

###Non-printed Parts:
 	
* Additional Hardware:
	* **Suggested Spring 1** listed below (**x21**)
	* **Suggested Spring 2** listed below (**x5**)
	* **Suggested Nuts** listed below (**x42**)
	* **Suggested Bolts** listed below (**x21**)
	* 1/4" #4 Drive Screw listed below (**x8**) for mounting the BOARD_HOLDER and OpenBCI Board
* Wiring (**x21**)
	* We strip apart the [Gold Cup Electrodes](http://openbci.myshopify.com/collections/frontpage/products/openbci-gold-cup-electrodes) or from the Touch-Proof Connector cable that comes with an [OpenBCI 32bit Board Kit](http://openbci.myshopify.com/collections/frontpage/products/openbci-32-bit-board-kit).
* Dry electrodes by Florida Research Instruments
	* (**18x**) Dry (spikey) electrodes to be installed in Ultracortex nodes with hair: [Disposable / Reusable Dry EEG Electrode ($0.60 each at 50+ quantity purchase) ](http://fri-fl-shop.com/product/tde-200/)
	* (**3x**) Dry (non-spikey) electrodes to be installed in Ultracortex nodes without hair (forehead, for instance): [Disposable / Reusable Cup Wet/Dry EEG Electrode ($10.00 for 15) ](http://fri-fl-shop.com/product/disposable-reusable-dry-eeg-electrode-quantity-of-15-tde-200a1/)
	* (**2x**) Ear Clip electrode (for reference): [TDI-430 Silver-Silver Chloride Ear Clip Electrode ($19.95 each)](http://fri-fl-shop.com/product/td-430-silver-disc-electrode-ear-clip/)
* (**1x**) An [OpenBCI 32bit Board](http://openbci.myshopify.com/collections/frontpage/products/openbci-32-bit-board-kit) or an [OpenBCI 16-channel R&D Kit](http://openbci.myshopify.com/collections/frontpage/products/openbci-16-channel-r-d-kit)
* (**1x**) Lithium Ion Rechargeable Battery Pack (~500mAh) — [Sparkfun](https://www.sparkfun.com/products/10718) or [Adafruit](http://www.adafruit.com/products/1578)
* (**1x**) [A charger for your battery pack](https://www.adafruit.com/products/1304)
* (**~10x**) [Zip tie](http://www.amazon.com/Black-Zip-Tie-100-Bag/dp/B0001IMMJI)

## THE COMPLETE ULTRACORTEX (w/ PICTURES)

###3D-printed Parts:

####(1x) FRAME

* [FRAME](https://github.com/OpenBCI/Ultracortex/tree/master/Mark_III_Nova/STLs/FRAME) (head circumference: small = 50-55cm, medium = 55-60cm, large = 60-65cm)
	* FRAME_FRONT (**x1**) — .STLs ([small](https://github.com/OpenBCI/Ultracortex/raw/master/Mark_III_Nova/STLs/FRAME/small/FRAME_FRONT_small.stl) / [medium](https://github.com/OpenBCI/Ultracortex/raw/master/Mark_III_Nova/STLs/FRAME/medium/FRAME_FRONT_medium.stl) / [large](https://github.com/OpenBCI/Ultracortex/raw/master/Mark_III_Nova/STLs/FRAME/large/FRAME_FRONT_large.stl))
	* FRAME_BACK (**x1**) — .STLs ([small](https://github.com/OpenBCI/Ultracortex/raw/master/Mark_III_Nova/STLs/FRAME/small/FRAME_BACK_small.stl) / [medium](https://github.com/OpenBCI/Ultracortex/raw/master/Mark_III_Nova/STLs/FRAME/medium/FRAME_BACK_medium.stl) / [large](https://github.com/OpenBCI/Ultracortex/raw/master/Mark_III_Nova/STLs/FRAME/large/FRAME_BACK_large.stl))



####(21x) MECH_PARTS

* [MECH_PARTS](https://github.com/OpenBCI/Ultracortex/tree/master/Mark_III_Nova/STLs/MECH_PARTS)
	* [OCTANUT](https://github.com/OpenBCI/Ultracortex/blob/master/Mark_III_Nova/STLs/MECH_PARTS/OCTANUT.stl) (**x21**) — [.STL download link](https://github.com/OpenBCI/Ultracortex/raw/master/Mark_III_Nova/STLs/MECH_PARTS/OCTANUT.stl)
	* [OCTABOLT](https://github.com/OpenBCI/Ultracortex/blob/master/Mark_III_Nova/STLs/MECH_PARTS/OCTABOLT.stl) (**x29**) — [.STL download link](https://github.com/OpenBCI/Ultracortex/raw/master/Mark_III_Nova/STLs/MECH_PARTS/OCTABOLT.stl)
	* [OCTARING](https://github.com/OpenBCI/Ultracortex/blob/master/Mark_III_Nova/STLs/MECH_PARTS/OCTARING.stl) (**x8**) — [.STL download link](https://github.com/OpenBCI/Ultracortex/raw/master/Mark_III_Nova/STLs/MECH_PARTS/OCTARING.stl)
	* [E_HOLDER](https://github.com/OpenBCI/Ultracortex/blob/master/Mark_III_Nova/STLs/MECH_PARTS/E_HOLDER.stl) (**x29**) — [.STL download link](https://github.com/OpenBCI/Ultracortex/raw/master/Mark_III_Nova/STLs/MECH_PARTS/E_HOLDER.stl)
	* [QUADSTAR](https://github.com/OpenBCI/Ultracortex/blob/master/Mark_III_Nova/STLs/MECH_PARTS/QUADSTAR.stl) (**x8**) — [.STL download link](https://github.com/OpenBCI/Ultracortex/raw/master/Mark_III_Nova/STLs/MECH_PARTS/QUADSTAR.stl)
	* [Comfy Insert](https://github.com/OpenBCI/Ultracortex/blob/master/Mark_III_Nova/STLs/MECH_PARTS/Comfy_Insert.stl) (**x13**) — [.STL download link](https://github.com/OpenBCI/Ultracortex/raw/master/Mark_III_Nova/STLs/MECH_PARTS/Comfy_Insert.stl)	

 

####(1x) BOARD_HOLDER

* BOARD_HOLDER (**x1**)
	* [BOARD_HOLDER](https://github.com/OpenBCI/Ultracortex/blob/master/Mark_III_Nova/STLs/HOLDER_AND_COVER/BOARD_COVER_STANDARD.stl) — [.STL download link](https://github.com/OpenBCI/Ultracortex/raw/master/Mark_III_Nova/STLs/HOLDER_AND_COVER/BOARD_COVER_STANDARD.stl)	
 

####(1x) BOARD_COVER

* BOARD_COVER (**x1**) — choose STANDARD or ADVANCED
	* [STANDARD](https://github.com/OpenBCI/Ultracortex/blob/master/Mark_III_Nova/STLs/HOLDER_AND_COVER/BOARD_COVER_STANDARD.stl) — [.STL download link](https://github.com/OpenBCI/Ultracortex/raw/master/Mark_III_Nova/STLs/HOLDER_AND_COVER/BOARD_COVER_STANDARD.stl)
	* [ADVANCED](https://github.com/OpenBCI/Ultracortex/blob/master/Mark_III_Nova/STLs/HOLDER_AND_COVER/BOARD_COVER_ADVANCED.stl) (for extra hardware accessibility / if you've soldered on your header rows) — [.STL download link](https://github.com/OpenBCI/Ultracortex/raw/master/Mark_III_Nova/STLs/HOLDER_AND_COVER/BOARD_COVER_ADVANCED.stl)

 




###Non-printed Parts:

####Suggested springs: 

* Suggested Spring 1 (**x21**) — aka "Weak Spring" — [Century Spring Corp. Stock #: U-4](http://cad.centuryspring.com/db/service?domain=century&command=showProduct&category=compression&product=U-4) — this spring is not as strong as spring 2. We use it to mount the electrodes. The low "Rate" (1.3 lbs/in) makes it more forgiving and comfortable when holding the spikey electrode against your head. This process is described in more detail below (in the "Assembly Instructions" section).



* Suggested Spring 2 (**x5**) — aka "Strong Spring" — [Century Spring Corp. Stock #: S-713](http://cad.centuryspring.com/db/service?domain=century&command=showProduct&category=compression&product=S-713) — this spring has a much stronger "Rate" (14 lb/in). This makes is ideal to act as a standoff at locations where you do not have a spikey electrode. This process is described in more detail below (in the "Assembly Instructions" section).



####Suggested nuts/bolts:

We use small stainless steel screws and hex nuts to fasten the FRI electrodes (listed above) to the 3D-printed electrode mount components &  wiring that connects the electrodes back to the OpenBCI board. We used stripped [Gold Cup Electrodes](http://openbci.myshopify.com/collections/frontpage/products/openbci-gold-cup-electrodes) as the cabling, by removing the gold cup with a wire cutter and looping the exposed wire around the screw between the two tightened hex nuts (as seen in the picture below).

* (**21x**) [Stainless Steel Pan Head Phillips Machine Screw, 2-56 Thread, 3/4" Length ($5.70 per pack of 50)](http://www.mcmaster.com/#91772a084/=11zdicn)
* (**42x**) [Stainless Steel Hex Nut, 2-56 Thread Size, 3/16" Wide, 1/16" High](http://www.mcmaster.com/#91841a003/=xzahv0)



####Suggested screws for fastening BOARD_MOUNT & OpenBCI Board

* (**8x**) [#4 Drive Screw](http://www.mcmaster.com/#90077a106/=yysd5f)



####Wiring

* (**21x**) We strip apart the [Gold Cup Electrodes](http://openbci.myshopify.com/collections/frontpage/products/openbci-gold-cup-electrodes)) or the Touch-Proof Connector cable that comes with an [OpenBCI 32bit Board Kit](http://openbci.myshopify.com/collections/frontpage/products/openbci-32-bit-board-kit).



####Dry electrodes by Florida Research Instruments

* (**18x**) Dry (spikey) electrodes to be installed in Ultracortex nodes with hair: [Disposable / Reusable Dry EEG Electrode ($0.60 each at 50+ quantity purchase) ](http://fri-fl-shop.com/product/tde-200/)
* (**3x**) Dry (non-spikey) electrodes to be installed in Ultracortex nodes without hair (forehead, for instance): [Disposable / Reusable Cup Wet/Dry EEG Electrode ($10.00 for 15) ](http://fri-fl-shop.com/product/disposable-reusable-dry-eeg-electrode-quantity-of-15-tde-200a1/)
* (**2x**) Ear Clip electrode (for reference): [TDI-430 Silver-Silver Chloride Ear Clip Electrode ($19.95 each)](http://fri-fl-shop.com/product/td-430-silver-disc-electrode-ear-clip/)



####(1x) An [OpenBCI 32bit Board](http://openbci.myshopify.com/collections/frontpage/products/openbci-32-bit-board-kit) (8 electrode channels) or an [OpenBCI 16-channel R&D Kit](http://openbci.myshopify.com/collections/frontpage/products/openbci-16-channel-r-d-kit) (16 electrode channels)



####(**1x**) ~500mAh lithium ion rechargeable battery pack ([Sparkfun](https://www.sparkfun.com/products/10718) or [Adafruit](http://www.adafruit.com/products/1578)) & (**1x**) [A charger for your battery pack](https://www.adafruit.com/products/1304)



#### (**~10x**) [Zip tie](http://www.amazon.com/Black-Zip-Tie-100-Bag/dp/B0001IMMJI)



## SUGGESTED PRINT SETTINGS

* FRAME_FRONT & FRAME_BACK
	* Material: PLA
	* Supports: YES
	* Raft: hopefully NO (but if supports aren't sticking, try the raft)
	* Infill: 20%
	* Layer Height: 0.2mm
	* Number of Shells: 3
	* Speed while extruding: 50-70% (slow it down if possible; these parts are detailed)
* MECH_PARTS (OCTANUT / BOLT / SPRING_CASING / ELECTRODE_HOLDER)
	* Material: PLA
	* Supports: NO
	* Raft: NO
	* Infill: 20%
	* Layer Height: 0.2mm
	* Number of Shells: 3
	* Speed while extruding: 50-70% (slow it down if possible; these parts are detailed)
* BOARD_MOUNT, BOARD_COVER_STANDARD, & BOARD_COVER_ADVANCED
	* Material: PLA
	* Supports: NO
	* Raft: NO
	* Infill: 20%
	* Layer Height: 0.2mm
	* Number of Shells: 3
	* Speed while extruding: 50-70% (slow it down if possible; these parts are detailed)

## RECOMMENDED ASSEMBLY TOOLS

1. [Loctite Super Glue w/ Cyanoacrylate](http://www.amazon.com/Loctite-1365882-20-Gram-Bottle-Professional/dp/B004Y960MU/ref=sr_1_1?s=automotive&ie=UTF8&qid=1440204266&sr=1-1&keywords=loctite+cyanoacrylate&pebp=1440204267936&perid=0HJQ0FB9G4J9SEBQBVGA)
2. coarse flat & circular files (for removing support artifacts)
3. medium sand paper
4. exacto blade
5. philips head screw driver
6. wire cutters
7. needle-nose pliers
8. snippers



## ASSEMBLY INSTRUCTIONS

### Remove residual support material & print flaws

Use sand paper, a file, and snippers to clean your FRAME and other 3D-printed parts. The most important part of this process is that you thoroughly clean out the frames nodes where you will place your OCTANUT pieces.




### Glue the FRAME together

Carefully, glue the FRAME_FRONT and FRAME_BACK together with your Cyanoacrylate super glue. The best way to do this is to place both halves of the frame on a level surface and carefully bring them together. Be sure to be precise; it's VERY difficult to pull the pieces apart once you've put them together.



### Mount the OpenBCI BOARD_HOLDER

First, use a 1/16" drillbit to expand the holes on the Ultracortex frame. This will make it easier to screw the BOARD_HOLDER on the frame.



Use four #4 Drive Screws to mount the BOARD_HOLDER to the FRAME. Make sure that the orientation of the BOARD_HOLDER matches that of the pictures below:



### Assemble the Comfort Nodes

In order to fit the OCTANUT pieces into the frame, you will need the Comfort Nodes in order to securely glue the OCTANUTs in place. 

You will need the following pieces:

-OCTABOLT

-Strong Spring

-ELECTRODE_HOLDER

-Comfort insert



First, put the comfort insert into front of the ELECTRODE_HOLDER.


Next, insert the spring into the back of the ELECTRODE_HOLDER.


Then, slide the OCTABOLT over the top:



### Insert OCTANUT pieces (x21) into frame

**Note:** at each node, you must line up the cut in the OCTANUT with the indentation on the frame as indicated in the picture below.



For each OCTANUT, insert the OCTABOLT so that the OCTANUT is held into the frame. Now you can glue the OCTANUT to the frame like this:



Your Ultracortex should now look like this:



### Embed OpenBCI into the Ultracortex

Connect your ~500 mAh lithium ion rechargeable batter to the back of your 32bit OpenBCI Board. Then fold the battery and its wires neatly behind the board before inserting the board into the BOARD_MOUNT. You can then use one of your #4 Drive Screws to secure the OpenBCI Board to the BOARD_MOUNT. Typically you don't need to use any #4 Drive Screws because the BOARD_COVER locks the OpenBCI Board in place, but in this case it's a good idea because you'll want to see where you're connecting your wires.





### Identify electrode locations

Before creating your electrode mounts, it's a good idea to think about where you may want to place the electrodes on the Ultracortex FRAME. The placement of the electrode may affect how long you make the wire between the electrode and where the OpenBCI is mounted, at the back of the frame.

The Ultracortex node locations are based on the [10-20 system](https://goo.gl/gSwYw), which is the internationally accepted standard for electrode placement in the context of EEG.

The images below indicates the default 10-20 electrode locations that the OpenBCI Graphical User Interface expects. This application is great for viewing/recording your EEG and can be found in our [OpenBCI_Processing](http://) repo. The blue nodes indicate the 8 default 10-20 locations (channels 1-8) of the 32bit Board. The red nodes indicate the default 10-20 locations of channels 9-16 when using the OpenBCI 16-channel R&D Kit. 

For the remainder of this tutorial, the blue nodes on the 10-20 system diagram (channels 1-8 of the OpenBCI default settings) will be used. The channel to 10-20 system correlations are as follows:

* Channel 1 - Fp1
* Channel 2 - Fp2
* Channel 3 - C3
* Channel 4 - C4
* Channel 5 - P7
* Channel 6 - P8
* Channel 7 - O1
* Channel 8 - O2



### Connect wiring to OpenBCI

Before shortening any of your wires, connect the female header of each wire to the N pin of channels 1-8, as indicated in the image to the lower right. The N pins are the ones closer to the OpenBCI Board. By default, the OpenBCI Board references these 8 pins with the SRB 2 pin (the bottom SRB pin).



### Measure, cut, and strip wires

For each wire, measure the distance between where it is connected to the OpenBCI Board and the node that it will terminate at on the Ultracortex frame. Give yourself 2-3 inches of slack (extra length), because you're going to strip the end of the wire, and you may want the extra slack to zip-tie/tape the wiring to the frame later on.

As mentioned above, if you're using the default OpenBCI electrode configuration, cut the wires so that they terminate at the following nodes:

* Channel 1 - Fp1
* Channel 2 - Fp2
* Channel 3 - C3
* Channel 4 - C4
* Channel 5 - P7
* Channel 6 - P8
* Channel 7 - O1
* Channel 8 - O2

After you're done measuring, cutting, and stripping your wires, disconnect them from the OpenBCI board. You will need the female header free so you can guide the springs and OCTANUT pieces into place in the following step. But remember which wire goes where!









### Assemble electrode mounts (x8 or x16)
**Note:** repeat the following steps as many times as necessary, depending upon your OpenBCI setup. In general, using more electrodes will distribute the downward scalp pressure, increasing comfort. Additionally, to increase comfort you can create electrode units without electrodes and the wires to place at various nodes around the frame. This will also help to distribute  pressure.

These are the pieces that comprise one full electrode unit:


First, slide a **Machine Screw (2-56 Thread, 3/4" Length)** through the FRI electrode and guide it into the ELECTRODE_HOLDER.



Then, slide the screw and electrode into the ELECTRODE_HOLDER


Next, twist a *Hex Nut (2-56 Thread Size, 3/16" Wide, 1/16" High)* onto the screw, securing the electrode to the holder.


Next, twist the exposed metal of your wire so that it is tight and clean.



This part is a little bit tricky! Wrap the exposed metal of your wire once around the remaining thread of the screw. You can use your finger nail to pinch the wire down against the nut, while wrapping. 




Then, twist your second Hex Nut onto the screw, securing the wire between the two nuts. You can use wire cutters to firmly screw the nut into place.



Slide a **Suggested Spring 1 (aka "Weak Spring")** and then the OCTABOLT around the wire as shown below.



Snap the full electrode unit together, guiding the semi-spherical protrusions on the outside of the SPRING_CASING into the relief cuts of the OCTABOLT. 



Voila! Spring-loaded electrode GIF!



### Insert electrode units into your Ultracortex

Once you've asesembled all of your electrode units, twist them into their respective Ultracortex frame nodes. If the parts are tough to twist into place by hand, use the OCTATOOL that comes with your kit as shown in the picture below. Over time the resistance between the OCTANUT and OCTABOLT will diminish, and the pieces will twist into place more easily.



### Reconnect wires to OpenBCI & connect ear clip electrodes (Reference & Ground)

Now that all of your electrode units are connected to your Ultracortex frame, reconnect the electrode wires to the OpenBCI board as detailed above. If you have some handy, you may want to use zip ties to secure the loose wiring to the Ultracortex frame. Later revisions of the headset will be designed to account for this. ;)



Next, connect two touch-proof adapter cables to SRB2 and bottom BIAS pin (white and black respectively in the image below). You can use the touch-proof adapter that comes with the OpenBCI 32bit Board or OpenBCI 16-channel R&D Kit. Then connect your [ear clip electrodes](http://fri-fl-shop.com/product/td-430-silver-disc-electrode-ear-clip/) to these touch-proof adapters. These ear clip electrodes serve as the reference and bias (ground with common-mode noise rejection) for your EEG system.

Alternatively, cut the earclip wire to about a foot long. Cut the touch-proof adapter wire to 2 inches long. Solder these two wires together, and shrink wrap them or wrap them in electrical tape.



For the 16 channel board, cut and solder two wires to the ear clip wire as shown:





### Fasten the BOARD_COVER

Now clip your board cover into place. If you've soldered any of the header rows onto your OpenBCI board, you'll need to use the BOARD_COVER_ADVANCED, as seen in the picture below. Otherwise, you can use the BOARD_COVER_STANDARD with the OpenBCI logo.



## Supernova Add-Ons

### Parts



To add the QUADSTAR extensions to your Supernova, use the following parts:

**3D Printed Parts**

* [Quadstar](https://github.com/OpenBCI/Ultracortex/blob/master/Mark_III_Nova/STLs/MECH_PARTS/QUADSTAR.stl) (**8X**) -- [.STL download link](https://github.com/OpenBCI/Ultracortex/raw/master/Mark_III_Nova/STLs/MECH_PARTS/QUADSTAR.stl)
* [Octaring](https://github.com/OpenBCI/Ultracortex/blob/master/Mark_III_Nova/STLs/MECH_PARTS/OCTARING.stl) (**8X**) -- [.STL download link](https://github.com/OpenBCI/Ultracortex/raw/master/Mark_III_Nova/STLs/MECH_PARTS/OCTANUT.stl)

**Non-3D Printed Parts**

* Zip ties

### Stretch QUADSTAR over OCTARING

Take your QUADSTAR and stretch it so that it fits over the OCTARING



### Zip Tie QUADSTAR onto frame

Using zip ties, tie down the corners of the QUADSTAR onto the frame of your ULTRACORTEX. You should be using four zip ties per QUADSTAR. For QUADSTARS that are next to each other, re-use the same zip tie to tie them both down to the frame. NOTE: Tie the QUADSTARS down loosely at first in order to ensure that they are all centered while tied down to the frame. Once all of the QUADSTARS are tied loosely to the frame, tighten them to secure them to the frame.






### Cut Zip Ties

Turn the ULTRACORTEX over and snip off all of the loose ends of the zip ties.



### Insert Comfort Nodes

Next, screw a comfort node into each of the 8 QUADSTARS.



### Supernova Assembly Complete!


### Adjust the Ultracortex for your head

Put the Ultracortex Mark 3 onto your head and gradually tighten the electrode units until the electrodes are snuggly (but comfortably) against your scalp. If it is difficult to twist the OCTABOLT pieces by hand, you may need to use the OCTATOOL as seen in the gif below. 

**Be careful** not to strain the electrode wires when twisting the electrode unit with the OCTATOOL, or you may separate the wire from the electrode itself. Turn the OCTABOLT until the wire is nearly taught, then reposition the wire and tool and twist again, as demonstrated in the gif.



### Examine your brain waves!

Place your UltraCortex on your head so that the back center node is roughly the same distance above your inion (bump on the back of your skull) as the front center node is above the bridge of your nose. As you place the UltraCortex on your head, the springs should adjust to the shape and size of your head.

Now that you have your Ultracortex assembled and comfortably adjusted to your head size and shape, it's brain wave time!



Check out the [Getting Started w/ OpenBCI tutorial](http://docs.openbci.com/tutorials/01-GettingStarted) to get up-and-running with the [OpenBCI Processing GUI](https://github.com/OpenBCI/OpenBCI_Processing).

Below is a screenshot of what the GUI looks like when you've got your OpenBCI + Ultracortex (w/ 8 channels) hooked up! You can see a nice alpha (~11 hz) spike on the FFT Plot. 



### Give Us Feedback!

If you have questions, comments, or suggestions regarding the printing and/or assembly of the Ultracortex, we'd love to hear from you. Please submit issues to this repository or email us at [contact@openbci.com](mailto:contact@openbci.com). Or take some pictures of yourself wearing the Ultracortex and Tweet at us ([@OpenBCI](https://twitter.com/OpenBCI) & [@Ultracortex](https://twitter.com/Ultracortex))!

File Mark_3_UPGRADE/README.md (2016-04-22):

#Ultracortex Mark 3 (UPGRADE)
*Development Period: July 2015 — September 2015*



####Complete Ultracortex Mark 3 kits are [available for sale](http://openbci.myshopify.com/collections/frontpage/products/ultracortex-mark-3-eeg-headset-kit-assembly-required) in the OpenBCI Online Store!

The Ultracortex is an open-source, 3D-printable headset intended to work with the [OpenBCI system](http://openbci.com/). It is capable of recording research-grade brain activity (EEG), muscle activity (EMG), and heart activity (ECG). The Ultracortex is under constant iteration. If you print/assemble your own Ultracortex, we would love to hear your feedback. Send us an email at [contact@openbci.com](mailto:contact@openbci.com) or Tweet at us ([@Ultracortex](https://twitter.com/Ultracortex) & [@OpenBCI](https://twitter.com/OpenBCI))!

Designers & Engineers:

* [Aaron Trocola (aka Threeform)](http://threeformfashion.com/)
* [Conor Russomanno](https://twitter.com/russomanno15)
* [Joel Murphy (aka SafeForRobots)](https://twitter.com/safeforrobots)

## THE COMPLETE ULTRACORTEX

**Note:** the part quantities listed below assume you are making an electrode holder for all 21 nodes of the Ultracortex Mark 3. In reality, you will likely have only 8 or 16 electrodes, depending on whether you are working with the [OpenBCI 32bit Board](http://openbci.myshopify.com/collections/frontpage/products/openbci-32-bit-board-kit) (8 channels) or the [OpenBCI 16-channel R&D Kit](http://openbci.myshopify.com/collections/frontpage/products/openbci-16-channel-r-d-kit) (16 channels). You may only want to create as many electrode units as you have channels, and then add more as necessary. In general, more electrodes will distribute the downward scalp pressure, increasing comfort.

###3D-printed Parts:

* [FRAME](https://github.com/OpenBCI/Ultracortex/tree/master/Mark_3_UPGRADE/STLs/FRAME) (head circumference: small = 50-55cm, medium = 55-60cm, large = 60-65cm)
	* FRAME_FRONT (**x1**) — .STLs ([small](https://github.com/OpenBCI/Ultracortex/raw/master/Mark_3_UPGRADE/STLs/FRAME/small/FRAME_FRONT_small.stl) / [medium](https://github.com/OpenBCI/Ultracortex/raw/master/Mark_3_UPGRADE/STLs/FRAME/medium/FRAME_FRONT_medium.stl) / [large](https://github.com/OpenBCI/Ultracortex/raw/master/Mark_3_UPGRADE/STLs/FRAME/large/FRAME_FRONT_large.stl))
	* FRAME_BACK (**x1**) — .STLs ([small](https://github.com/OpenBCI/Ultracortex/raw/master/Mark_3_UPGRADE/STLs/FRAME/small/FRAME_BACK_small.stl) / [medium](https://github.com/OpenBCI/Ultracortex/raw/master/Mark_3_UPGRADE/STLs/FRAME/medium/FRAME_BACK_medium.stl) / [large](https://github.com/OpenBCI/Ultracortex/raw/master/Mark_3_UPGRADE/STLs/FRAME/large/FRAME_BACK_large.stl))
* [MECH_PARTS](https://github.com/OpenBCI/Ultracortex/tree/master/Mark_3_UPGRADE/STLs/MECH_PARTS)
	* [OCTANUT](https://github.com/OpenBCI/Ultracortex/blob/master/Mark_3_UPGRADE/STLs/MECH_PARTS/OCTANUT.stl) (**x21**) — [.STL download link](https://github.com/OpenBCI/Ultracortex/raw/master/Mark_3_UPGRADE/STLs/MECH_PARTS/OCTANUT.stl)
	* [OCTABOLT](https://github.com/OpenBCI/Ultracortex/blob/master/Mark_3_UPGRADE/STLs/MECH_PARTS/OCTABOLT.stl) (**x21**) — [.STL download link](https://github.com/OpenBCI/Ultracortex/raw/master/Mark_3_UPGRADE/STLs/MECH_PARTS/OCTABOLT.stl)
	* [OCTARING](https://github.com/OpenBCI/Ultracortex/blob/master/Mark_3_UPGRADE/STLs/MECH_PARTS/OCTARING.stl) (**x21**) — [.STL download link](https://github.com/OpenBCI/Ultracortex/raw/master/Mark_3_UPGRADE/STLs/MECH_PARTS/OCTARING.stl)
	* [ELECTRODE_HOLDER](https://github.com/OpenBCI/Ultracortex/blob/master/Mark_3_UPGRADE/STLs/MECH_PARTS/E_HOLDER.stl) (**x21**) — [.STL download link](https://github.com/OpenBCI/Ultracortex/raw/master/Mark_3_UPGRADE/STLs/MECH_PARTS/E_HOLDER.stl)
	* [WEB](https://github.com/OpenBCI/Ultracortex/blob/master/Mark_3_UPGRADE/STLs/MECH_PARTS/WEB.stl) (**x21**) — [.STL download link](https://github.com/OpenBCI/Ultracortex/raw/master/Mark_3_UPGRADE/STLs/MECH_PARTS/WEB.stl)
	* [Comfy Insert](https://github.com/OpenBCI/Ultracortex/blob/master/Mark_3_UPGRADE/STLs/MECH_PARTS/Comfy_Insert.stl) (**x21**) — [.STL download link](https://github.com/OpenBCI/Ultracortex/raw/master/Mark_3_UPGRADE/STLs/MECH_PARTS/Comfy_Insert.stl)	
* [BOARD_HOLDER](https://github.com/OpenBCI/Ultracortex/blob/master/Mark_3_UPGRADE/STLs/BOARD_HOLDER.stl) (**x1**) — [.STL download link](https://github.com/OpenBCI/Ultracortex/raw/master/Mark_3_UPGRADE/STLs/BOARD_HOLDER.stl)
* BOARD_COVER (**x1**) — choose STANDARD or ADVANCED
	* [STANDARD](https://github.com/OpenBCI/Ultracortex/blob/master/Mark_3_UPGRADE/STLs/BOARD_COVER_STANDARD.stl) — [.STL download link](https://github.com/OpenBCI/Ultracortex/raw/master/Mark_3_UPGRADE/STLs/BOARD_COVER_STANDARD.stl)
	* [HOLDER](https://github.com/OpenBCI/Ultracortex/blob/master/Mark_3_UPGRADE/STLs/BOARD_COVER_STANDARD.stl) — [.STL download link](https://github.com/OpenBCI/Ultracortex/raw/master/Mark_3_UPGRADE/STLs/BOARD_COVER_STANDARD.stl)	
	* [ADVANCED](https://github.com/OpenBCI/Ultracortex/blob/master/Mark_3_UPGRADE/STLs/BOARD_COVER_ADVANCED.stl) (for extra hardware accessibility / if you've soldered on your header rows) — [.STL download link](https://github.com/OpenBCI/Ultracortex/raw/master/Mark_3_UPGRADE/STLs/BOARD_COVER_ADVANCED.stl)

###Non-printed Parts:
 	
* Additional Hardware:
	* **Suggested Spring 1** listed below (**x21**)
	* **Suggested Spring 2** listed below (**x5**)
	* **Suggested Nuts** listed below (**x42**)
	* **Suggested Bolts** listed below (**x21**)
	* 1/4" #4 Drive Screw listed below (**x8**) for mounting the BOARD_HOLDER and OpenBCI Board
* Wiring (**x21**)
	* We strip apart the [Gold Cup Electrodes](http://openbci.myshopify.com/collections/frontpage/products/openbci-gold-cup-electrodes) or from the Touch-Proof Connector cable that comes with an [OpenBCI 32bit Board Kit](http://openbci.myshopify.com/collections/frontpage/products/openbci-32-bit-board-kit).
* Dry electrodes by Florida Research Instruments
	* (**18x**) Dry (spikey) electrodes to be installed in Ultracortex nodes with hair: [Disposable / Reusable Dry EEG Electrode ($0.60 each at 50+ quantity purchase) ](http://fri-fl-shop.com/product/tde-200/)
	* (**3x**) Dry (non-spikey) electrodes to be installed in Ultracortex nodes without hair (forehead, for instance): [Disposable / Reusable Cup Wet/Dry EEG Electrode ($10.00 for 15) ](http://fri-fl-shop.com/product/disposable-reusable-dry-eeg-electrode-quantity-of-15-tde-200a1/)
	* (**2x**) Ear Clip electrode (for reference): [TDI-430 Silver-Silver Chloride Ear Clip Electrode ($19.95 each)](http://fri-fl-shop.com/product/td-430-silver-disc-electrode-ear-clip/)
* (**1x**) An [OpenBCI 32bit Board](http://openbci.myshopify.com/collections/frontpage/products/openbci-32-bit-board-kit) or an [OpenBCI 16-channel R&D Kit](http://openbci.myshopify.com/collections/frontpage/products/openbci-16-channel-r-d-kit)
* (**1x**) Lithium Ion Rechargeable Battery Pack (~500mAh) — [Sparkfun](https://www.sparkfun.com/products/10718) or [Adafruit](http://www.adafruit.com/products/1578)
* (**1x**) [A charger for your battery pack](https://www.adafruit.com/products/1304)
* (**~10x**) [Zip tie](http://www.amazon.com/Black-Zip-Tie-100-Bag/dp/B0001IMMJI)

## THE COMPLETE ULTRACORTEX (w/ PICTURES)

###3D-printed Parts:

####(1x) FRAME

* [FRAME](https://github.com/OpenBCI/Ultracortex/tree/master/Mark_3_UPGRADE/STLs/FRAME) (head circumference: small = 50-55cm, medium = 55-60cm, large = 60-65cm)
	* FRAME_FRONT (**x1**) — .STLs ([small](https://github.com/OpenBCI/Ultracortex/raw/master/Mark_3_UPGRADE/STLs/FRAME/small/FRAME_FRONT_small.stl) / [medium](https://github.com/OpenBCI/Ultracortex/raw/master/Mark_3_UPGRADE/STLs/FRAME/medium/FRAME_FRONT_medium.stl) / [large](https://github.com/OpenBCI/Ultracortex/raw/master/Mark_3_UPGRADE/STLs/FRAME/large/FRAME_FRONT_large.stl))
	* FRAME_BACK (**x1**) — .STLs ([small](https://github.com/OpenBCI/Ultracortex/raw/master/Mark_3_UPGRADE/STLs/FRAME/small/FRAME_BACK_small.stl) / [medium](https://github.com/OpenBCI/Ultracortex/raw/master/Mark_3_UPGRADE/STLs/FRAME/medium/FRAME_BACK_medium.stl) / [large](https://github.com/OpenBCI/Ultracortex/raw/master/Mark_3_UPGRADE/STLs/FRAME/large/FRAME_BACK_large.stl))

 

####(21x) MECH_PARTS

[MECH_PARTS](https://github.com/OpenBCI/Ultracortex/tree/master/Mark_3_UPGRADE/STLs/MECH_PARTS)
	* [OCTANUT](https://github.com/OpenBCI/Ultracortex/blob/master/Mark_3_UPGRADE/STLs/MECH_PARTS/OCTANUT.stl) (**x21**) — [.STL download link](https://github.com/OpenBCI/Ultracortex/raw/master/Mark_3_UPGRADE/STLs/MECH_PARTS/OCTANUT.stl)
	* [OCTABOLT](https://github.com/OpenBCI/Ultracortex/blob/master/Mark_3_UPGRADE/STLs/MECH_PARTS/OCTABOLT.stl) (**x21**) — [.STL download link](https://github.com/OpenBCI/Ultracortex/raw/master/Mark_3_UPGRADE/STLs/MECH_PARTS/OCTABOLT.stl)
	* [OCTARING](https://github.com/OpenBCI/Ultracortex/blob/master/Mark_3_UPGRADE/STLs/MECH_PARTS/OCTARING.stl) (**x21**) — [.STL download link](https://github.com/OpenBCI/Ultracortex/raw/master/Mark_3_UPGRADE/STLs/MECH_PARTS/OCTARING.stl)
	* [ELECTRODE_HOLDER](https://github.com/OpenBCI/Ultracortex/blob/master/Mark_3_UPGRADE/STLs/MECH_PARTS/E_HOLDER.stl) (**x21**) — [.STL download link](https://github.com/OpenBCI/Ultracortex/raw/master/Mark_3_UPGRADE/STLs/MECH_PARTS/E_HOLDER.stl)
	* [WEB](https://github.com/OpenBCI/Ultracortex/blob/master/Mark_3_UPGRADE/STLs/MECH_PARTS/WEB.stl) (**x21**) — [.STL download link](https://github.com/OpenBCI/Ultracortex/raw/master/Mark_3_UPGRADE/STLs/MECH_PARTS/WEB.stl)
	* [Comfy Insert](https://github.com/OpenBCI/Ultracortex/blob/master/Mark_3_UPGRADE/STLs/MECH_PARTS/Comfy_Insert.stl) (**x21**) — [.STL download link](https://github.com/OpenBCI/Ultracortex/raw/master/Mark_3_UPGRADE/STLs/MECH_PARTS/Comfy_Insert.stl)	

 

####(1x) BOARD_HOLDER

* BOARD_HOLDER (**x1**)
	* [BOARD_HOLDER](https://github.com/OpenBCI/Ultracortex/blob/master/Mark_3_UPGRADE/STLs/BOARD_COVER_STANDARD.stl) — [.STL download link](https://github.com/OpenBCI/Ultracortex/raw/master/Mark_3_UPGRADE/STLs/BOARD_COVER_STANDARD.stl)	
 

####(1x) BOARD_COVER

* BOARD_COVER (**x1**) — choose STANDARD or ADVANCED
	* [STANDARD](https://github.com/OpenBCI/Ultracortex/blob/master/Mark_3_UPGRADE/STLs/BOARD_COVER_STANDARD.stl) — [.STL download link](https://github.com/OpenBCI/Ultracortex/raw/master/Mark_3_UPGRADE/STLs/BOARD_COVER_STANDARD.stl)
	* [ADVANCED](https://github.com/OpenBCI/Ultracortex/blob/master/Mark_3_UPGRADE/STLs/BOARD_COVER_ADVANCED.stl) (for extra hardware accessibility / if you've soldered on your header rows) — [.STL download link](https://github.com/OpenBCI/Ultracortex/raw/master/Mark_3_UPGRADE/STLs/BOARD_COVER_ADVANCED.stl)

 




###Non-printed Parts:

####Suggested springs: 

* Suggested Spring 1 (**x21**) — aka "Weak Spring" — [Century Spring Corp. Stock #: U-4](http://cad.centuryspring.com/db/service?domain=century&command=showProduct&category=compression&product=U-4) — this spring is not as strong as spring 2. We use it to mount the electrodes. The low "Rate" (1.3 lbs/in) makes it more forgiving and comfortable when holding the spikey electrode against your head. This process is described in more detail below (in the "Assembly Instructions" section).



* Suggested Spring 2 (**x5**) — aka "Strong Spring" — [Century Spring Corp. Stock #: S-845](http://cad.centuryspring.com/db/service?domain=century&command=showProduct&category=compression&product=S-845) — this spring has a much stronger "Rate" (14 lb/in). This makes is ideal to act as a standoff at locations where you do not have a spikey electrode. This process is described in more detail below (in the "Assembly Instructions" section).



####Suggested nuts/bolts:

We use small stainless steel screws and hex nuts to fasten the FRI electrodes (listed above) to the 3D-printed electrode mount components &  wiring that connects the electrodes back to the OpenBCI board. We used stripped [Gold Cup Electrodes](http://openbci.myshopify.com/collections/frontpage/products/openbci-gold-cup-electrodes) as the cabling, by removing the gold cup with a wire cutter and looping the exposed wire around the screw between the two tightened hex nuts (as seen in the picture below).
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

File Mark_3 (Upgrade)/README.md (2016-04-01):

#Ultracortex Mark 3
*Development Period: July 2015 — September 2015*



####Complete Ultracortex Mark 3 kits are [available for sale](http://openbci.myshopify.com/collections/frontpage/products/ultracortex-mark-3-eeg-headset-kit-assembly-required) in the OpenBCI Online Store!
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

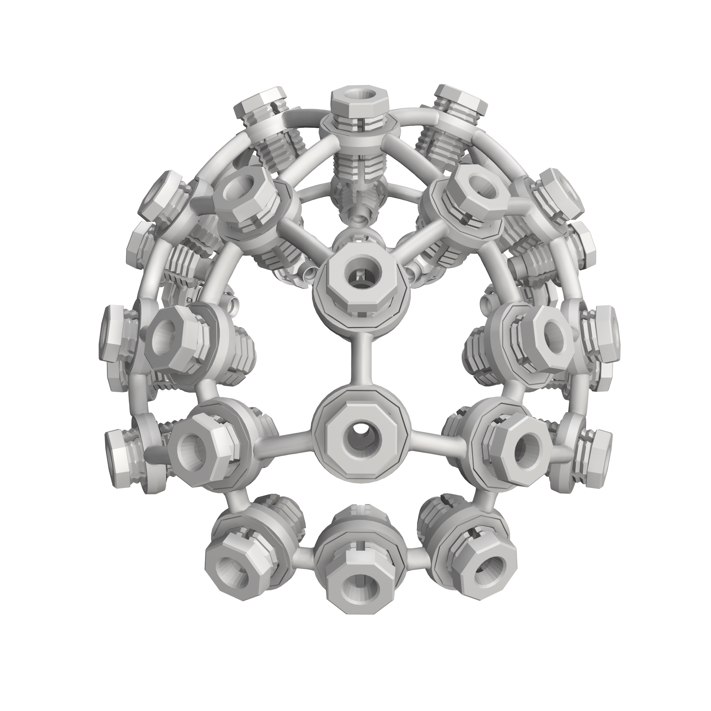
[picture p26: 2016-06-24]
Mark_IV/concepts/M4-June16/Photos/M4_08_D5_Front Perspective.png

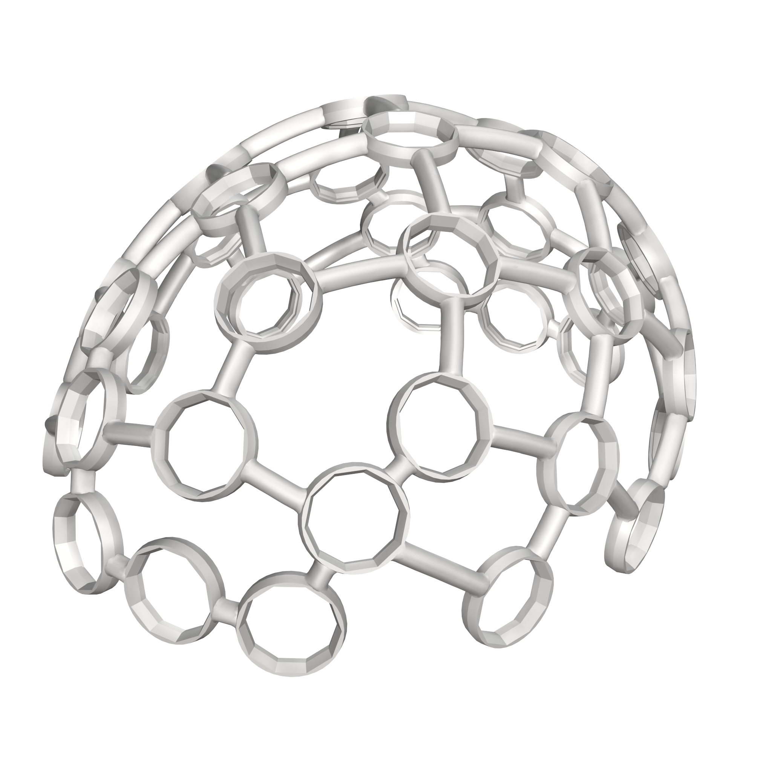
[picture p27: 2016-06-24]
Mark_IV/concepts/M4-June16/Photos/M4_08_D5_Angle_Frame only.png

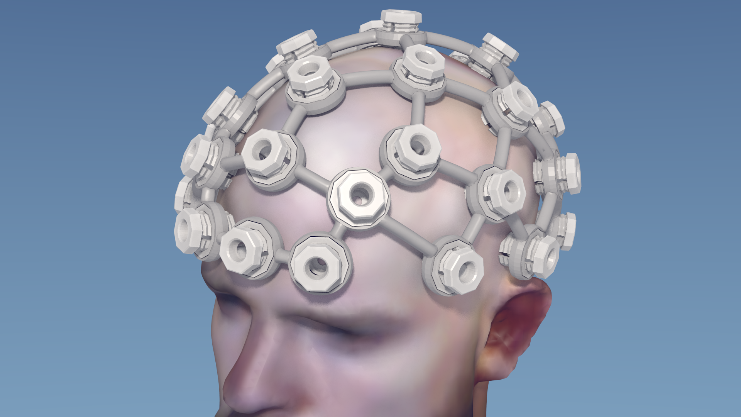
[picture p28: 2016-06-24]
Mark_IV/concepts/M4-June16/Photos/M4_08_D5_frame228_Realistic1.png

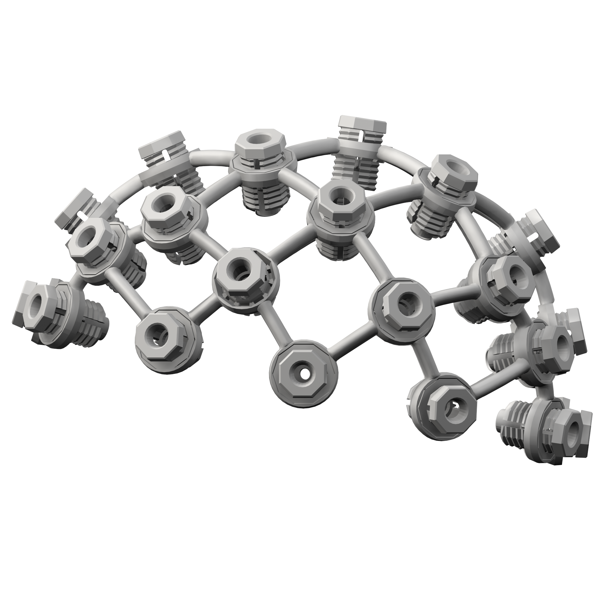
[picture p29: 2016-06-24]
Mark_IV/concepts/M4-June16/Photos/M4_08_D5_Side.png

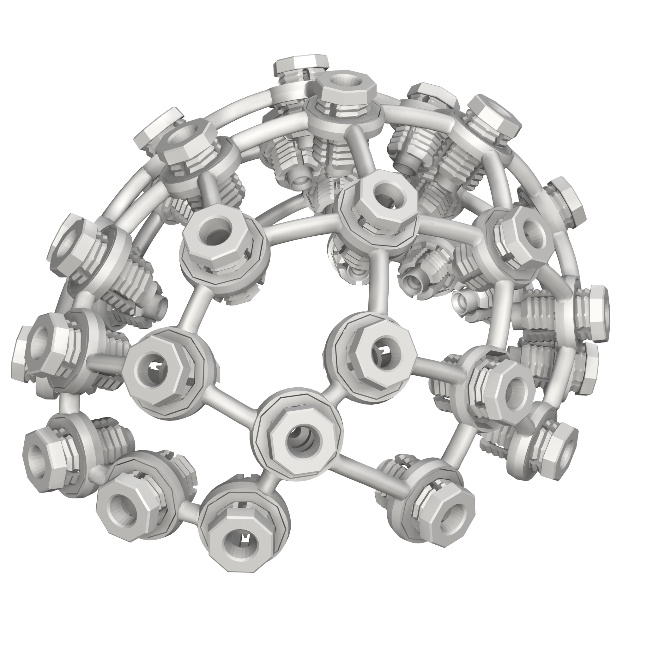
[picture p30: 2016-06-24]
Mark_IV/concepts/M4-June16/Photos/M4_08_D5_Angle.png

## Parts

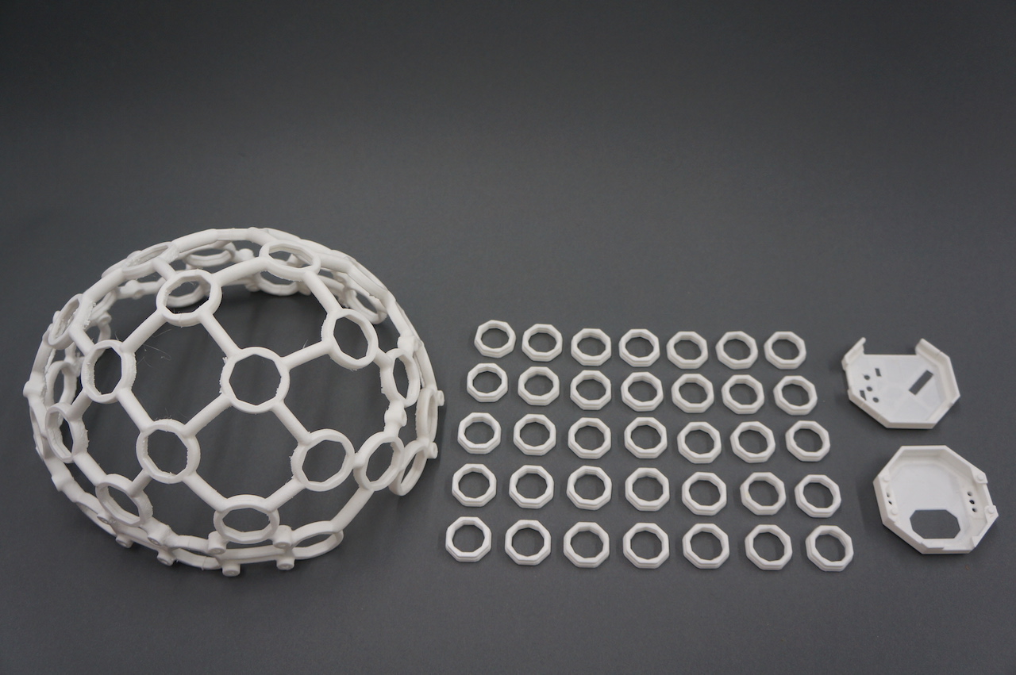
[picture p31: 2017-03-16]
Mark_IV/MarkIV-FINAL/Photos/3D_printed_Parts2.JPG

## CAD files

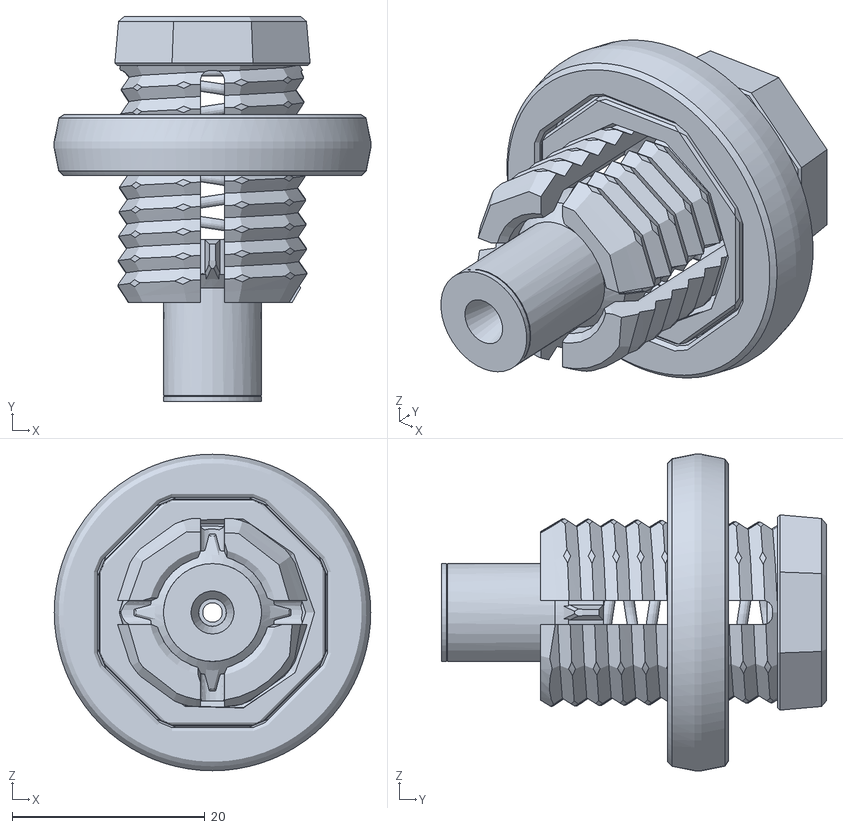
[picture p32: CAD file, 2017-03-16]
Mark_IV/DevKit/M4 Hardware/M4_Hardware_10_Complete Assembly.stl
32.9 x 40.0 x 32.9

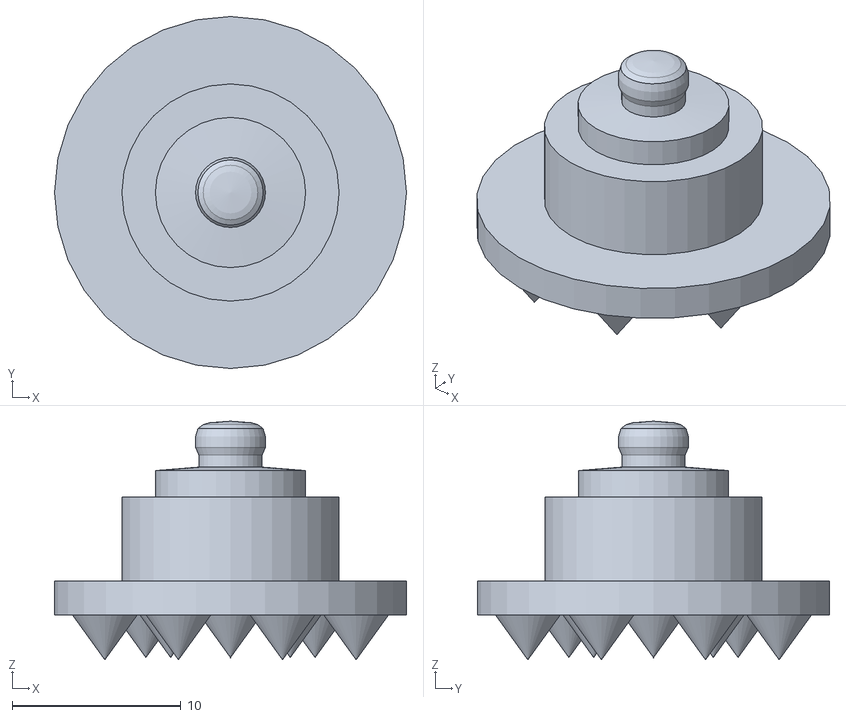
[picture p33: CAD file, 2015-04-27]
Mark_1/Electrode1.stl
20.9 x 20.9 x 14.2

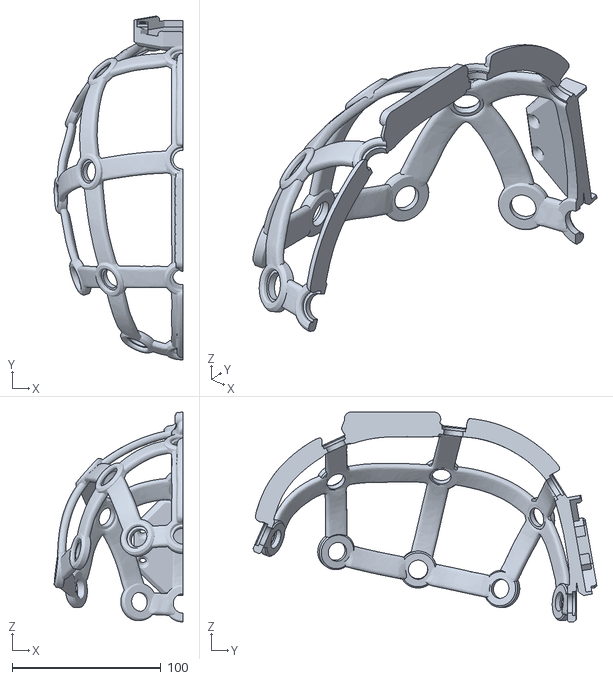
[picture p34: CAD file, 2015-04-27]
Mark_1/OpenBCI_Headset_halves_with holder/OpenBCI test1c_Union4_right_with holder.STL
86.4 x 231.2 x 141.2

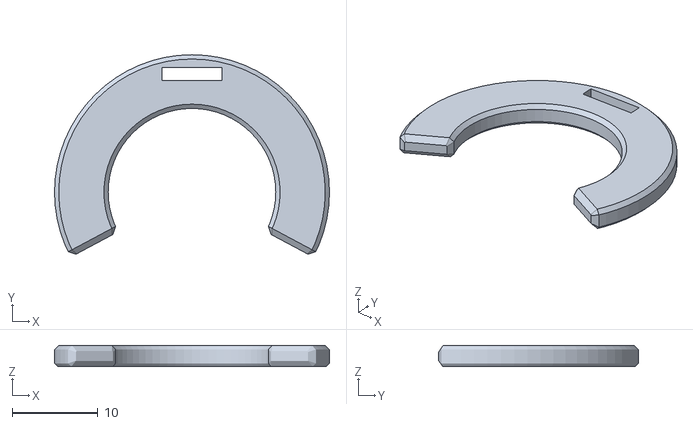
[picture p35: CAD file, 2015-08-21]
Mark_2/STLs/M2-Electrode-Mount/SPACER_NEW_1.stl
32.0 x 23.2 x 2.50

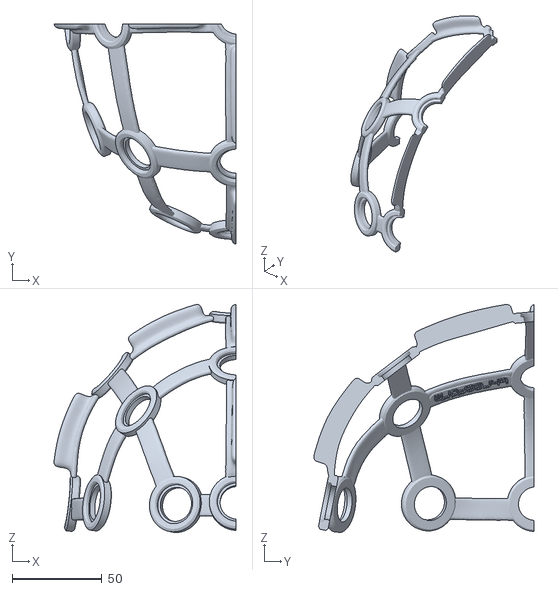
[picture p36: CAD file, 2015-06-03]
Mark_2/STLs/M2-Frame/UltraCortex_M2_front right2.stl
101.2 x 122.6 x 126.8

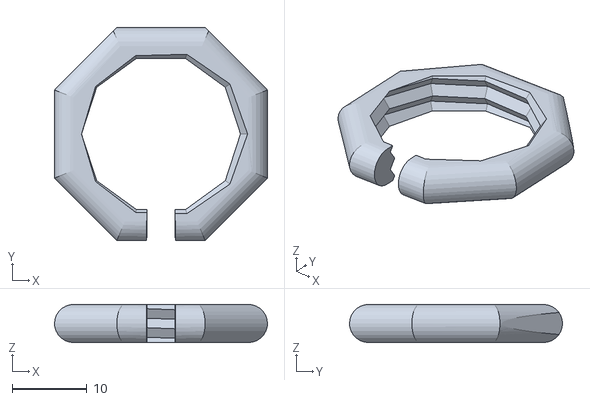
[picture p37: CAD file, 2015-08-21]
Mark_3/LATEST_STLs/OCTANUT_MODIFIED_99innerThread.stl
28.4 x 28.4 x 5.08

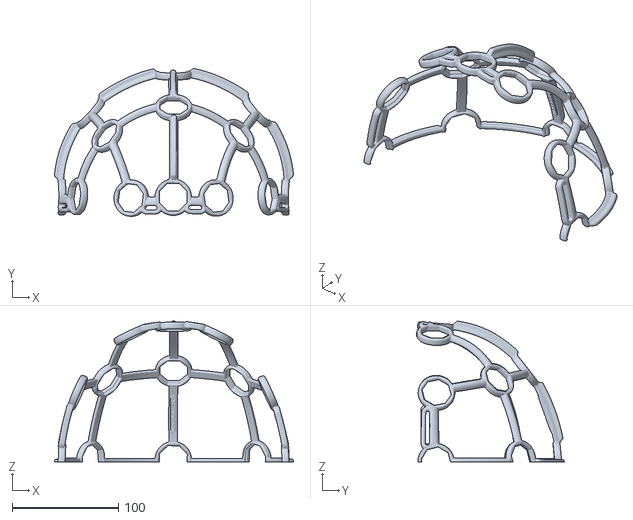
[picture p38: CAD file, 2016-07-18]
Mark_III_Nova_REVISED/STLs/FRAME/large/LARGE_FRONT-M3_Nova_Revised.stl
224.9 x 139.1 x 132.3

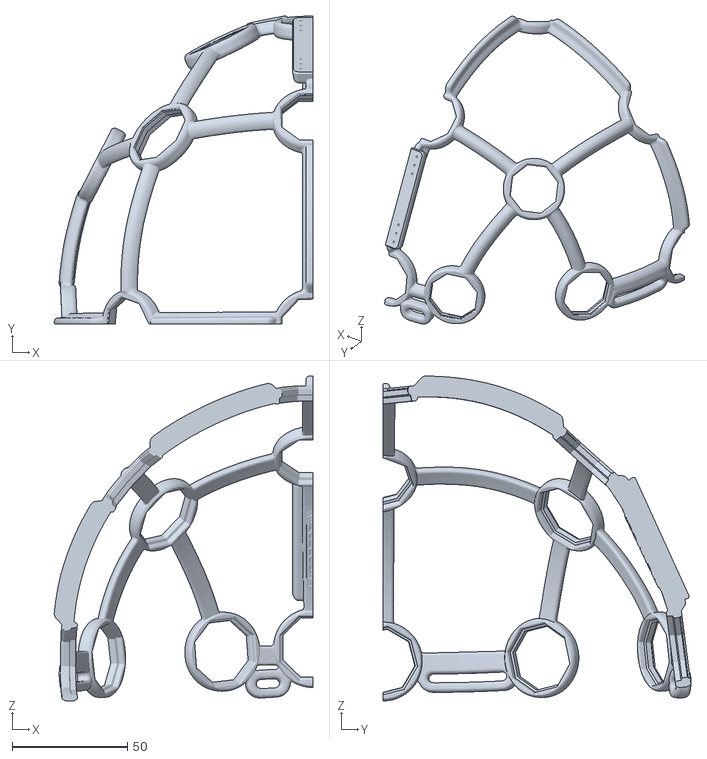
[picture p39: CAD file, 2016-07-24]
Mark_III_Nova_REVISED/STLs/FRAME/large/LARGE_QUADS/M3P_large_back_right.stl
112.1 x 133.5 x 140.9

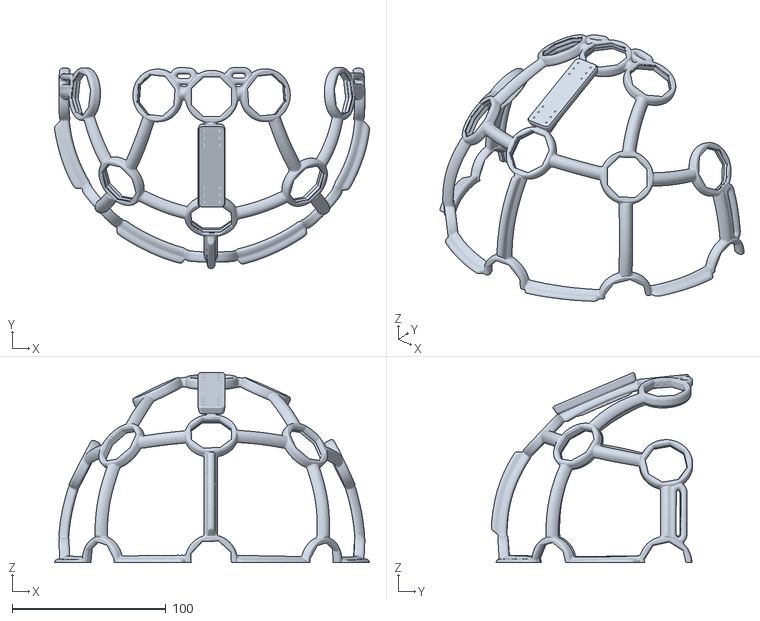
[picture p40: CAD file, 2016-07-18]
Mark_III_Nova_REVISED/STLs/FRAME/medium/MEDIUM_BACK-M3_Nova_Revised.stl
204.9 x 131.1 x 123.7

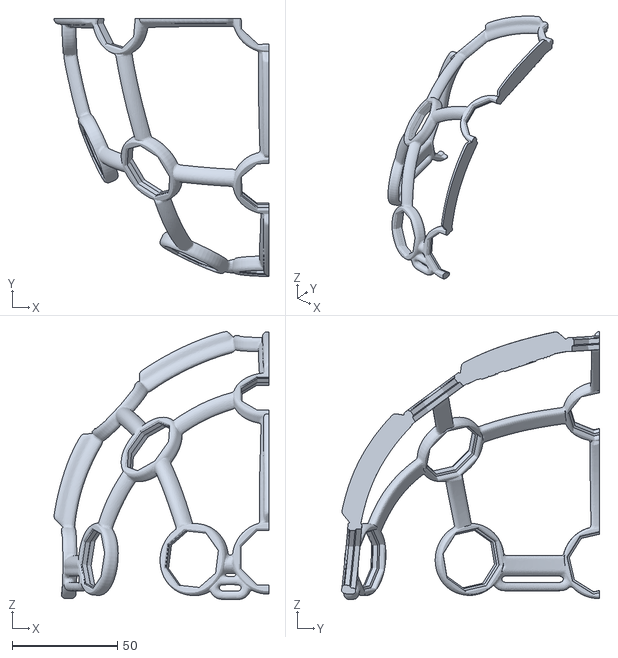
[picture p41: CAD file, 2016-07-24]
Mark_III_Nova_REVISED/STLs/FRAME/medium/MEDIUM_QUADS/M3P_medium_front_right.stl
102.2 x 122.7 x 127.4

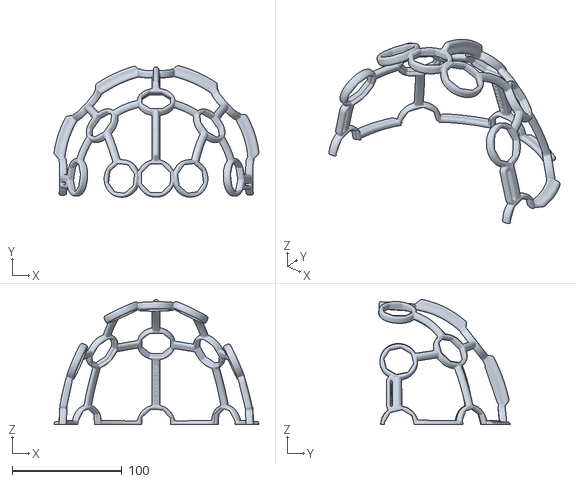
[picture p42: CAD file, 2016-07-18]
Mark_III_Nova_REVISED/STLs/FRAME/small/SMALL_FRONT-M3_Nova_Revised.stl
187.0 x 120.2 x 114.1

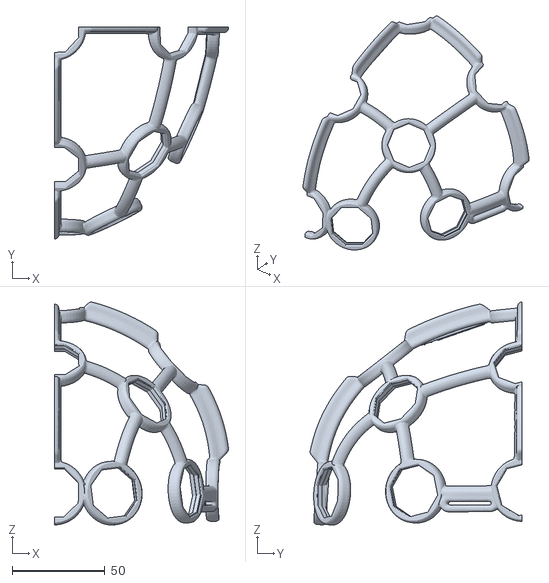
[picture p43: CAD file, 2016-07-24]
Mark_III_Nova_REVISED/STLs/FRAME/small/SMALL_QUADS/M3P_small_front_left.stl
93.8 x 114.1 x 120.1

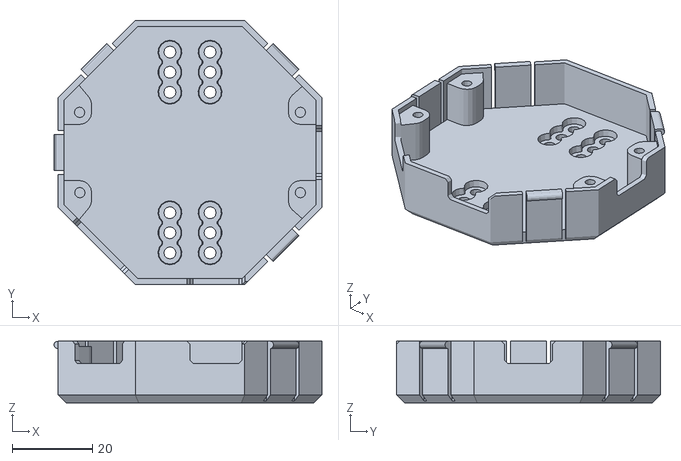
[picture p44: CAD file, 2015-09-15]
Mark_III_Nova_REVISED/STLs/HOLDER_AND_COVER/BOARD_HOLDER.stl
66.8 x 65.8 x 15.4

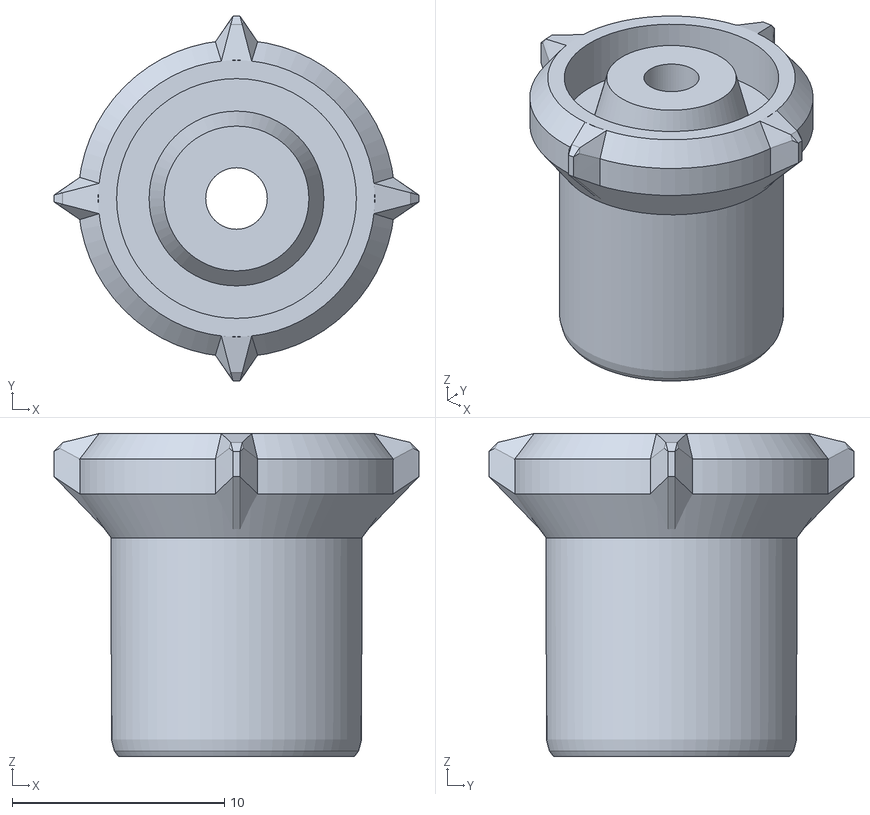
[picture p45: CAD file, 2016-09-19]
Mark_III_Nova_REVISED/STLs/MECH_PARTS/E_HOLDER.stl
17.2 x 17.2 x 15.2

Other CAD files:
Mark_III_Nova_REVISED/STLs/MECH_PARTS/OCTANUT/OCTANUT-LOOSE.stl
Mark_IV/concepts/M4-June16/M4_D5_V9_loops_Small_halves/M4_D5_V9_loops_Small_back.stl
Mark_IV/concepts/M4-June16/M4_D5_V9_Small.stl
Mark_IV/concepts/M4-June16/M4_D5_V9_Small_halves/M4_D5_Small_front.stl
Mark_1/FRI_electrode_mount.stl
Mark_1/OpenBCI_Headset_halves_with holder/OpenBCI test1c_Union4_left_with holder.STL
Mark_2/STLs/M2-Electrode-Mount/M2_Electrode Mount A_01.STL
Mark_2/STLs/M2-Electrode-Mount/M2_Electrode Mount B_01.STL
Mark_2/STLs/M2-Electrode-Mount/M2_Electrode Spacer_01.STL
Mark_2/STLs/M2-Frame/UltraCortex_M2_back left2.stl
Mark_2/STLs/M2-Frame/UltraCortex_M2_back right2.stl
Mark_2/STLs/M2-Frame/UltraCortex_M2_front left2.stl
Mark_3/LATEST_STLs/BOLT.stl
Mark_3/LATEST_STLs/ELECTRODE_HOLDER.stl
Mark_3/LATEST_STLs/FRAME_BACK.stl
Mark_3/LATEST_STLs/FRAME_FRONT.stl
Mark_3/LATEST_STLs/SPRING_CASING_modified.stl
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

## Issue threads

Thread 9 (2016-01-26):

OpenBCI/Ultracortex #9: .prt file request -- to edit in Solidworks

momonala, 2016-01-26:
Hi, 
We're using openBCI for a senior thesis project to make audiovisual feedback from eeg, ekg, and mmg. We're lovin openBCI, but we're starting to think about headset design. We want to make a few edits to the ultracortex, but the .stl files are not editable in solidworks. Can you post the original CAD files (.prt)? 

Much appreciation, 
Mohit

ThreeForm, 2016-12-16:
Mohit, We spoke via email about this, but I want to follow up on the open issue listing.

While the Ultracortex frame was not created in CAD (so there is no prt file), we made efforts to offer more useful data and files from the development of Ultracortex M4 so that people can modify it or make their own headset.  For CAD related files we offer an IGS files that contains the frame curves, constructions planes, and mounting points (a new M4 feature). Those who contacted us about CAD source (like yourself) are among the "beta" recipients of the templates, so I hope you'll offer us some feedback before we post the template.

momonala, 2016-12-27:
Hey,

Thanks for the update. The previous EEG project I was working on is in a
bit of a hiatus as the team has split up... Won't be much use for beta
testing right now. But I am excited to get my Ganglion next month!
Hopefully some new project ideas will spark up then.

Thanks,
Mohit

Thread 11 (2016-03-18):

OpenBCI/Ultracortex #11: Where are the Mark 4 files?

strfry, 2016-03-18:
The Mark 4 Model is already existing, judging from the pictures on http://shop.openbci.com/products/ultracortex-mark-iv

Why isn't it released yet?

teonbrooks, 2016-03-20:
hi @strfry, the Mark 4 is still in concept-phase. The STL will be released once the final product begins rolling out.

JFD-Mtl, 2016-03-28:
Do you have an expected release date ?

ThreeForm, 2016-05-02:
@strfry The Mark 4 is scheduled to be released in August 2016.

shruna, 2017-10-15:
Where are the bolts which holds electrodes on mark 4, are they same which are used in mark 3

teonbrooks, 2017-10-15:
@conorrussomanno ^

ThreeForm, 2017-10-15:
You can find the M4 bolt, and several variations of it, in the M4 [DevKit hardware section](https://github.com/OpenBCI/Ultracortex/tree/master/Mark_IV/DevKit/M4%20Hardware/Extended%20parts). The M4 bolt is smaller than M3 because of the higher node count in M4 (to stop them overlapping). They weren't in the original "Print your own" file release because the electrode assemblies are injection molded in the M4 kit. That means if you are not buying the electrode kit from OpenBCI you are going to have to source your own springs and electrodes, and you will need to either print your own bolt hardware or buy them on Shapeways here: [M4 headset parts on Shapeways](https://www.shapeways.com/shops/ultrabci)

closed 2022-09-29 by retiutut

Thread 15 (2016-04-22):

### ISSUE TITLE
Nova README, SRB1 -> SRB2

### ISSUE THREAD

**Issue by wjcroft** [OpenBCI/ultracortex#15]
Conor, Joel and team, great tutorial and design evolutions!

Minor typo, isn't the SRB pin closest to the board SRB2 and not SRB1 as stated in the README? It is clear from the photos that the pins closest to the board are used. But some other documentation, for example various places on the forum, shows reference on SRB2.

Cheers, William

**Comment by teonbrooks** [comment]
cc: @conorrussomanno

**Comment by gabrielibagon** [comment]
You are right! Edited "SRB1" to "SRB2" (bottom pin). This typo existed in the Mark 3 (original) documentation as well, so it's fixed there too. Thanks!

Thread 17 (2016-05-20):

### ISSUE TITLE
BOARD_HOLDER and BOARD_COVER stl download link for "Nova" headset CANNOT BE FOUND

### ISSUE THREAD

**Issue by wudixiaoxiami** [OpenBCI/ultracortex#17]
Hi all,
I encountered an issue on opening stl download link for board holder and cover of 'Nova' headset.

Can anyone post it again ?

Thank you very much.

Yuliang

**Comment by gabrielibagon** [comment]
Hi Yuliang,

I fixed the links for both board holder and cover in the readme, so they should work now. Thanks for catching that! 

Just for reference, there's a directory in the Ultracortex repo where you can download the stl files: https://github.com/OpenBCI/Ultracortex/tree/master/Mark_III_Nova/STLs

Gabe

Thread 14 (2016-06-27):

### ISSUE TITLE
Can anyone recommend a print-on demand service?

### ISSUE THREAD

**Issue by neuropil** [OpenBCI/ultracortex#14]
With a reasonable cost. 3D systems quoted ~4K.

Thanks!

**Comment by pattonsgirl** [comment]
Try Shapeways and i.materialize

**Comment by Tweakmind** [comment]
I recommend finding someone on 3DHubs.com

**Comment by teonbrooks** [comment]
@neuropil where are you based? IIRC @conorrussomanno mentioned that there is a service in NYC where you send them your file and one of the printing partners prints it and you can go pick it up. I am also think OpenBCI is within that network

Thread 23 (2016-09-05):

OpenBCI/Ultracortex #23: Battery charging?

Abraxas3d, 2016-09-05:
In the instructions about including the rechargeable battery, how is the charger included and connected?

"Embed OpenBCI into the Ultracortex

Connect your ~500 mAh lithium ion rechargeable batter to the back of your 32bit OpenBCI Board. Then fold the battery and its wires neatly behind the board before inserting the board into the BOARD_MOUNT. You can then use one of your #4 Drive Screws to secure the OpenBCI Board to the BOARD_MOUNT. Typically you don't need to use any #4 Drive Screws because the BOARD_COVER locks the OpenBCI Board in place, but in this case it's a good idea because you'll want to see where you're connecting your wires."

onyedikilo, 2017-02-01:
There is no charger, the batteries (which are not included) are AA size batteries. There is only a case to hold the batteries is included. You can also ditch the casing and use a Li-PO rechargeable battery. In both cases you will need to remove the battery and recharge and insert back again.

andreaortuno, 2017-03-13:
We recommend you purchase:

andreaortuno, 2017-03-13:
We recommend you purchase:

(2x) Lithium Ion Rechargeable Battery Pack (500mAh) from [Adafruit](https://www.adafruit.com/product/1578) or [Sparkfun](https://www.sparkfun.com/products/13851) — we recommend buying an extra battery so you can continue working while you recharge!
(1x) A charger for your battery pack ([Adafruit](https://www.adafruit.com/products/1304) or [Sparkfun](https://www.sparkfun.com/products/10217))

The batteries fit in the board case from the Ultracortex, but you will need to charge the batteries separately.

closed 2017-03-13 by andreaortuno

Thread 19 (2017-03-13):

### ISSUE TITLE
MARK IV - Medium and Large STL

### ISSUE THREAD

**Issue by jspenc72** [OpenBCI/ultracortex#19]
Can you post the stl for the medium and larger versions of the MARK IV?

**Comment by nielsswinkels** [comment]
Any news here? We just received our package so I would like to print the Mark IV, but with my big head printing the small size seems pointless.

**Comment by andreaortuno** [comment]
You can find all the files on the assembly guide:

**Comment by andreaortuno** [comment]
You can find all the files on the assembly guide:
https://github.com/OpenBCI/Docs/blob/master/Headware/01-Ultracortex-Mark-IV.md

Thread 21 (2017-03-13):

### ISSUE TITLE
possible corrosion problem observed when using recommended parts

### ISSUE THREAD

**Issue by Abraxas3d** [OpenBCI/ultracortex#21]
Using the parts listed for https://github.com/OpenBCI/Ultracortex/tree/master/Mark_III_Nova_REVISED, I observed the following.

There seems to be some sort of reaction or corrosion when putting together the electrodes and the machine screws. 

The photos (attached below) show an electrode as it comes out of the plastic shipping bag beside electrodes that have been assembled into their pods. 

The assembled pieces were put together 24 hours ago. One can observe what appears to be corrosion between the head of the screw and the electrode. 

They were not exposed to water. They were not screwed together very tightly. Electrical conductivity has not yet been affected, but if it continues, enough corrosion could prevent signals from conducting through the wire or being picked up at all. 

These are parts ordered directly off the links in the list on github. There were no substitutions. I did not use different parts. 

So... what's going on here? I shouldn't be seeing any corrosion between these parts, right? 

This is being built for a hackfest that will be held next week (10-11 September 2016)
https://sites.google.com/site/ieeebcihackathon/

![possiblecorrosionproblem-1705](https://cloud.githubusercontent.com/assets/6608613/18233324/cc9b098c-7298-11e6-8c2e-eff2b78b5f2e.jpg)
![possiblecorrosionproblem-1708](https://cloud.githubusercontent.com/assets/6608613/18233327/cc9cf094-7298-11e6-9485-7fc69cdeefb7.jpg)
![possiblecorrosionproblem-1709](https://cloud.githubusercontent.com/assets/6608613/18233325/cc9d1556-7298-11e6-8c67-47ae7e5fd21a.jpg)
![possiblecorrosionproblem-1714](https://cloud.githubusercontent.com/assets/6608613/18233326/cc9d21f4-7298-11e6-8183-3149ea8a7bf0.jpg)

**Comment by wjcroft** [comment]
See related forum post below, showing similar coloration changes. We suggest there to remove any possible oil or other coating from your bolts.

http://openbci.com/forum/index.php?p=/discussion/885/florida-research-dry-electrodes-corrosion-reaction-discoloration

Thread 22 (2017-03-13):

### ISSUE TITLE
Gold Cup Electrodes - not long enough for forehead electrodes

### ISSUE THREAD

**Issue by Abraxas3d** [OpenBCI/ultracortex#22]
Even when cutting off the no-touch connectors at their base, which gives the maximum length of the Gold Cup Electrodes wires, the length of the wire is simply not long enough to reach the forehead electrodes. 

I have a wire with the right connectors to make an extension for my build, but if someone tried to build this and didn't have that, it would be annoying. 

Has someone actually used these wires in constructing a headset? Have a photo? Maybe the Gold Cup Electrodes wires are shorter now than when they were specified? This is with a medium sized headset, so the problem would probably be worse for a large.

**Comment by onyedikilo** [comment]
The Gold Cup Electrode wires I received with 16 channel kit is 100cm in length.  No-touch connectors are 35cm in length.

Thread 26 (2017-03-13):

### ISSUE TITLE
Please update the repo with instructions for printing the mark IV

### ISSUE THREAD

**Issue by jspenc72** [OpenBCI/ultracortex#26]
Current instructions indicate that the model must be scaled before printing. I have tried printing per the instructions however the hardware does not fit. 

Please update repo with properly scaled stl files that don't require any modification and are ready to print. Please also add instructions with pictures detailing the assembly process for the mark IV.

**Comment by andreaortuno** [comment]
The instructions or on our docs repo. Here is the link: https://github.com/OpenBCI/Docs/blob/master/Headware/01-Ultracortex-Mark-IV.md

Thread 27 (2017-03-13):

### ISSUE TITLE
Make the frame more 3D printer friendly

### ISSUE THREAD

**Issue by MCTaylor17** [OpenBCI/ultracortex#27]
I showed this to our printer guy and he suggested:
> Whoa! Too large, too much support required, I would think that with our printer there would be a 0% chance of success. 

I'm wondering if there is a way to make this project more friendly a wider variety of 3D printers.  

Perhaps break the frame into smaller components would help?

**Comment by ThreeForm** [comment]
The design is optimized to use very little support. We have printed hundreds of units with few issues. The Mark IV in particular, with its diagonal frame, requires far less support. One problem we are noticing is innapropriate slicer settings being used. If your print looks like this: https://mobile.twitter.com/ultracortex/status/746351060344799232?p=v then you are doing it wrong. The default Cura settings on that 1-shot Lulzbot print used more material for support than for the frame, and the result was so locked in it was impossible to remove without breaking. Our recommendation is to print in halves (STL's provided in the assembly guide). On Makerbot Rep2 we use something like 72 degree support angle, and no raft, but do add some brim adhesion pieces manually. I cannot make a universal recommendation because each printer is different, but look at the slice preview. If it makes you say "whoa" then change your settings.

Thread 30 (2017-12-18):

OpenBCI/Ultracortex #30: STL files are not meant to be printed at home

tierralibre, 2017-12-18:
It would be great it the files were designed to be printed in to so not PRO 3d printing machines.

As well the orientation print way too much support. 

Please help!

ThreeForm, 2017-12-18:
The files print on normal size printers with a bed around 22cm. This includes the most popular machines like Prusa i3 (or clones), Ultimaker (or clones), Makerbot (or clones). All production units were made on MakerBot Rep2's and Lulzbot Taz5's.  Prusa clones can cost about $200, and are the most easily sourced printers around (though not as good quality as the original, obviously). Most people having trouble are using incorrect settings.  Make sure your orientation is correct. The flat side should be flat on the bed so the print is stable and doesn't need much support. Total support volume should be 10-20%.  More tips are available on the [OpenBCI Forum](http://openbci.com/forum/index.php?p=/discussion/1174/difficulty-3d-printing-tips-for-printing-from-aaron), or you can just buy an optimized nylon version of the frame on [Shapeways](https://www.shapeways.com/product/WKM73GNJM/m4-ultra-headset-frame?optionId=63113712).

Shootquinn, 2018-06-13:
I did some testing on this, and I have a couple of comments to make.

I got the "Whole Medium MkIV" to print in 14:34 on the Prusa Mk3 without supports. Of course there were issues with this approach, but I'm never afraid to push things. Later I printed one in 41:45 with supports set to 25 degrees in slic3r, which is about the minimum you can do on this before getting some of the failures showing up. 

The OP does have a point, although he isn't presenting it in a collaborative fashion. I do see that during the next redesign if an effort is made to minimize overhangs with asymetrical filleting, slightly changing the angles of the structures between one boss to another, etc., that the printing time can be reduced three fold and with a 15% cost savings based on your claim of support volume above. This would also make it more printable on less capable, cobbled together machines possibly in the 3rd world, support or no support. 

Thanks for keeping an open mind about this, I do love the design but there are some gains to be made as far as the printability goes. 

Note on my 14.5 hour print, it still has more usable bosses than easier versions of the Ultracortex. It could be put in service. 

Quinn

[image]

[image]

[image]

closed 2022-09-29 by retiutut

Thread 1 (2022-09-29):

### ISSUE TITLE
wrong electrodes

### ISSUE THREAD

**Issue by MarcusWolschon** [OpenBCI/ultracortex#1]
This doesn't look anywhere near like the electrodes that came with the OpenBCI V3 and there is no part list telling users to get any other ones.
Something doesn't match up here.

**Comment by conorrussomanno** [comment]
Marcus,

Sorry for the confusion. The electrodes seen in the photos here are dry electrodes from Florida Research Instruments (FRI), found here: http://fri-fl-shop.com/product/package-of-15-disposable-reusable-dry-electrodes-and-10-disposablereusable-eeg-cup-electrodes-and-5-leads-red-white-green-black-brown/

Conor

**Comment by MarcusWolschon** [comment]
That info should get into readme.md, not into this ticket.

**Comment by conorrussomanno** [comment]
Check the readme.md.

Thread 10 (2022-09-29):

### ISSUE TITLE
Head size

### ISSUE THREAD

**Issue by parthcmodi** [OpenBCI/ultracortex#10]
I noticed the STLs come in 3 different sizes (small, medium, and large).  What head sizes are they meant for?

**Comment by ThreeForm** [comment]
The frames correspond with these approximate head circumferences:
**Small = 50-55cm
Medium = 55-60cm
Large - 60-65cm**

The adjustment bolts create significant overlap between size ranges, so that the actual ranges overlap by 50%. A large headset fully adjusted inward (smaller) is approximately equivalent to a small headset adjusted outward (larger). A medium frame can fit an adult male about 90% of the time. Most women can wear an adjusted medium, but a small is usually a better fit.

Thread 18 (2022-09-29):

### ISSUE TITLE
QUADSTAR won't fit over OCTARING

### ISSUE THREAD

**Issue by alepirolo** [OpenBCI/ultracortex#18]
In the README.md is written "Take your QUADSTAR and stretch it so that it fits over the OCTARING" but we couldn't do it.
We tried by printing QUADSTAR bigger of 4% and of 5% but with this enlargment the OCTARING won't fit.
Can anyone explain how they managed to do this tricky part? Thank you

**Comment by onyedikilo** [comment]
Quadstar should be printed with a flexible material such as ninja flex, so that you can pull and stretch it to fit the octaring, no need to print it bigger.

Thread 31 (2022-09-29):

### ISSUE TITLE
Electrodes on the pictures

### ISSUE THREAD

**Issue by LeBovin** [OpenBCI/ultracortex#31]
Hey,

I would like to know if there is a tutorial to make the electrodes we can see on the Ultracortex IV's pictures ?

Thanks!

**Comment by ThreeForm** [comment]
LeBovin,
There currently is no Mark IV  electrode tutorial because the Mark IV uses
crimped connections for reliability. Electrodes that can be produced
manually would require a design change, but that will happen if enough
people ask for it.
Best,
 -Aaron

**Comment by LeBovin** [comment]
In this case, where could I buy the electrodes we can see in the pictures?

Thanks for you answer !

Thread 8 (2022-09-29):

### ISSUE TITLE
High Density EEG?

### ISSUE THREAD

**Issue by jpellman** [OpenBCI/ultracortex#8]
This might be more of a suggestion for a future project than an improvement on the present iteration of Ultracortex, but I thought I'd throw it out there anyways.

A small, but growing, number of researchers are scanning with 32, 64, 128 and 256 electrode systems in order to employ a technique called source localization.  Source localization, as its name implies, allows you to pinpoint where EEG signals are coming from in a way that gives spatial resolution reminiscent of fMRI (though not comparable; fMRI voxel sizes can be as low as 1 mm isotropic, while EEG voxel sizes tend to be around 5 mm isotropic).  This technique, though not without controversy (what scientific methodology isn't?) is something I would be interested in seeing become more prevalent, as it seems to me that it would be much more cost effective to gather large datasets with EEG than with fMRI.

There are some high density nets on the market today, and while they're cheaper than fMRI, they can still be rather pricey (upwards of a thousand dollars per net).  In a time of dwindling scientific budgets, these costs can be prohibitive to some labs that otherwise might have wanted to try using this technique.  In light of this, I think that it would be neat if there were an open source alternative that labs could try out (even if it weren't necessarily as fully-featured as the nets that are out right now).

Here are a couple links for you to check out concerning source localization if your interested:
http://cdasr.mclean.harvard.edu/content/publications/LATN/BookChapters/Pizzagalli_HandbookPhysiology07.pdf
http://neuroimage.usc.edu/brainstorm/Tutorials#Background_readings

**Comment by ThreeForm** [comment]
@jpellman Thanks for the links. We recognize the need for higher density, and since you wrote your message we have developed a headset (Ultracortex M4) with about 3x the node count of the original Ultracortex. Since the current OpenBCI board has up to 16 channels (using Daisy expansion), multiple boards would be required to fully populate the nodes of the current design.

For customers who want to focus on one area with higher density, we can build a custom headset with any electrode placement required. This is most practical if you need several headsets, but we can also custom fit to a particular subject using CT/MRI if needed.

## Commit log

2015-06-03 Mark 2 added
    new version ready to be printed!
    [UltraCortex_M2_back left2.stl, UltraCortex_M2_back right2.stl, UltraCortex_M2_front left2.stl, UltraCortex_M2_front right2.stl]
2015-06-03 Rep 2 prints added
    [UltraCortex_M2_back left2.stl, UltraCortex_M2_back right2.stl, UltraCortex_M2_front left2.stl, UltraCortex_M2_front right2.stl]
2015-06-03 Rearrange file structure (YIKES)
    [Electrode1.stl, FRI_electrode_mount.stl, OpenBCI test1c_Union4_left_with holder.STL, OpenBCI test1c_Union4_right_with holder.STL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]
2015-06-09 Electrode Added
    [M2_Electrode Mount A_01.STL, M2_Electrode Mount B_01.STL, M2_Electrode Spacer_01.STL, UltraCortex_M2_back left2.stl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]
2015-06-09 new print files added for Rep 2 Trodes
2015-06-10 added spring info
2015-08-20 M3 STLs added : )
    [M3_Back.stl, M3_Front.stl]
2015-08-21 Copy, Wipe, & Replace test.
    [BOLT.stl, ELECTRODE_HOLDER.stl, FRAME_BACK.stl, FRAME_FRONT.stl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]
2015-08-21 Modifications
    - Modified the inner thread of the OCTANUT to 99% in the x and y axis.
    The tolerance between it and the BOLT was too tight and the tolerance
    between the BOLT and the SPRING_CASING was more than enough.
    - Haven’t updated the FULLSET yet to reflect the new OCTANUT
    [OCTANUT.stl, OCTANUT_MODIFIED_99innerThread.stl]
2015-08-22 Deleted nonLATEST parts from LATEST FOLDER
    [FULLSET_MECHPARTS_x1.stl]
2015-08-28 added M3g hardware
    [M3g_Adjustment Bolt5.STL, M3g_Electrode Holder4b_Electrode mount.stl, M3g_Electrode Holder4b_spring cover.stl, M3g_NodeInsert6.STL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]
2015-08-29 M3k added
    [M3K6_back.stl, M3K6_front.stl, M3k5e_NodeSocket_09_1.35inch.STL, M3k_Adjustment Bolt6.STL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]
2015-09-04 Added some modified parts to M3k_InTesting/LATEST_STLs
    [ELECTRODE_HOLDER_M3m.stl, M3J_OpenBCI_holder4.STL, OCTABOLT_M3m.STL, OCTANUT_M3m.STL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]
2015-09-04 correction to modified parts... dropped .x3g, added .stl
    [OCTANUT_M3m_scaled102.stl]
2015-09-04 LATEST_FILES updated w/ new working versions of the M3
    [BACK_LEFT_M3K7.stl, BACK_M3K7.stl, BACK_RIGHT_M3K7.stl, BOARD_MOUNT.STL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]
2015-09-15 New 3D files, assembly instruction template, & folder structure
    [BACK_LEFT_M3K7.stl, BACK_M3K7.stl, BACK_RIGHT_M3K7.stl, BACK_large.stl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]
2015-09-16 updated assembly instructions
2015-09-16 Revert "updated assembly instructions"
    This reverts commit 433bd53f1d0cda360e980a57ab150ae8e23503ba.
2015-09-16 Revert "Revert "updated assembly instructions""
    This reverts commit b1a0e439e396b5f5efaebe5412ecb99f8058f246.
2015-09-16 Assembly instructions re-added
2015-09-16 Updating assembly instructions & combined readme
2015-09-16 assembly instructions update
2015-09-18 adding Rep2 print profiles
    [BACK_small.stl, BOARD_COVER_ADVANCED.stl, BOARD_COVER_STANDARD.stl, BOARD_COVER_advancedVersion.stl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]
2015-10-15 Improving Comfort w/ "Strong Spring Standoffs"
2015-10-23 Revert "updated readme.md"
    [BACK_LEFT_M3K7.stl, BACK_M3K7.stl, BACK_RIGHT_M3K7.stl, BACK_large.stl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]
2016-01-21 Mark III Updates
    - Updated OCTABOLT for better spring connection (lip & electrode hole
    90% of previous)
    - Updated MECHPARTS_x21 with new OCTABOLT part and made it x22—1 extra
    piece)
    - removed deprecated “PRINT_FILES”
    [OCTABOLT.stl]
2016-01-21 Updates Mark III
    [OCTABOLT_b.stl]
2016-01-21 Mark III Updates
    [OCTABOLT.stl]
2016-01-22 Fixing broken STL download links for board holder and covers
2016-03-31 M4 Early Concept Up
    Note: this will likely change substantially before the final MIV
    version!
    [E_HOLDER.stl, OCTABOLT.stl, OCTANUT.stl, SPRINGCASING.stl]
2016-04-01 Mark 3 Upgrade Tutorial
    [BACK_LEFT_M3K7.stl, BACK_M3K7.stl, BACK_RIGHT_M3K7.stl, BACK_large.stl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]
2016-04-13 changing UPGRADE directory name
    [BACK_LEFT_M3K7.stl, BACK_M3K7.stl, BACK_RIGHT_M3K7.stl, BACK_large.stl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]
2016-04-14 New STLs for MIII Upgrade
    [BACK_LEFT_M3K7.stl, BACK_M3K7.stl, BACK_RIGHT_M3K7.stl, BACK_large.stl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]
2016-04-15 pictures, guide edited for Nova
    [BOARD_COVER_ADVANCED.stl, BOARD_COVER_STANDARD.stl, BOARD_HOLDER.stl, Comfy_Insert.stl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]
2016-04-18 Nova & Supernova branded
    [BOARD_COVER_ADVANCED.stl, BOARD_COVER_STANDARD.stl, BOARD_HOLDER.stl, Comfy_Insert.stl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]
2016-04-18 III not 3
    Roman Numerals for the win!
    [BOARD_COVER_ADVANCED.stl, BOARD_COVER_STANDARD.stl, BOARD_HOLDER.stl, Comfy_Insert.stl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]
2016-04-29 supernova tutorial added
    [QUADSTAR.stl]
2016-04-29 new screw information
2016-04-29 updated strong spring link
2016-05-06 soldering instructions added
2016-06-24 MIII small frame added
2016-06-24 Reorganization of M4-June16
    [M4_D5_Small_back.stl, M4_D5_Small_front.stl, M4_D5_V9_Small.stl, M4_D5_V9__loops_Small.stl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]
2016-07-11 Adding MIII Nova Revised
    [BOARD_COVER_ADVANCED.stl, BOARD_COVER_STANDARD.stl, BOARD_HOLDER.stl, Comfy_Insert.stl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]
2016-07-18 NOVA REVISED new STLs added
    [FRAME_BACK_large.stl, FRAME_BACK_medium.stl, FRAME_BACK_small.stl, FRAME_FRONT_large.stl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]
2016-07-18 updated 1 link
    Niels, now it’s your turn!!!
2016-07-24 Nova/Supernova Frames — Now In 4 Parts! (QUADS - S/M/L)
    [M3P_large_back_left.stl, M3P_large_back_right.stl, M3P_large_front_left.stl, M3P_large_front_right.stl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]
2016-09-19 Fix boolean join error with simplyify 3d
    [E_HOLDER.stl]
2017-03-16 Adding Photos & STLs
    [M4 Board_Cover.stl, M4 Board_Mount.stl, M4_Hardware_insert_loose.STL, M4_Hardware_insert_tight.STL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]
2017-03-16 reorganization of directories
    [E_HOLDER.stl, M4_D5_Small_back.stl, M4_D5_Small_front.stl, M4_D5_V9_Small.stl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]
2017-03-16 Added Mark IV Dev Kit
    [LightCase_19H_Cover.stl, LightCase_19k_Frame.stl, LightCase_20b_Base.STEP, LightCase_20b_Base.STL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]
2017-09-18 changed the current product to Mark IV
2020-07-15 Adding Injection Molded STLs
    currently only available in archived UCM4 repo -- https://github.com/openbci-archive/Docs/tree/master/assets/MarkIV/STL_Directory/Injection_Molded_Parts
    [M4_Hardware_09_Eholder.STL, M4_Hardware_09_Octabolt.STL]
